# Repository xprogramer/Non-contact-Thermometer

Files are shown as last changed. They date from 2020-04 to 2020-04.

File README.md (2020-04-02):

# Non-contact-Thermometer v1.0
A low cost non-contact (infrared) Thermometer mainly based on Arduino and MLX90614 infrared temperature sensor

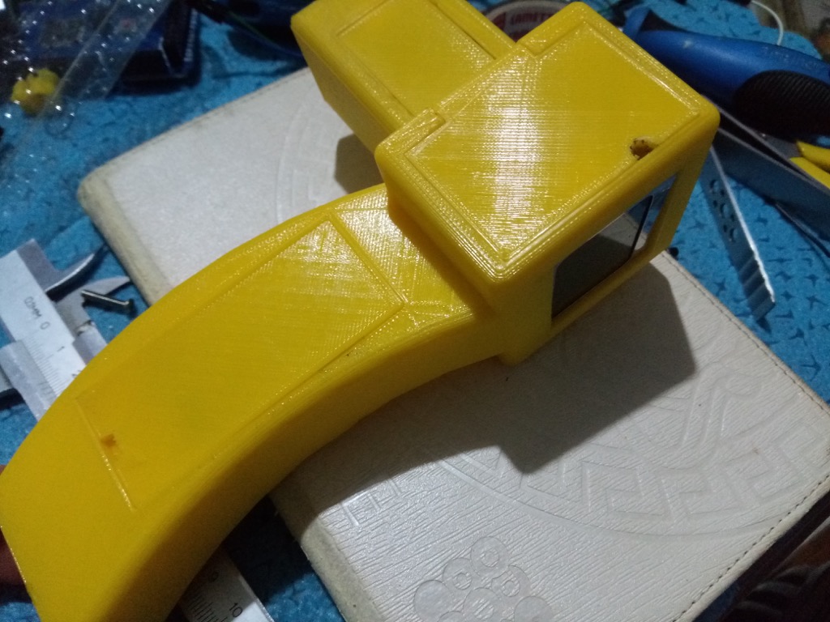
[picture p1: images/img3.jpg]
Infrared Thermometer image description


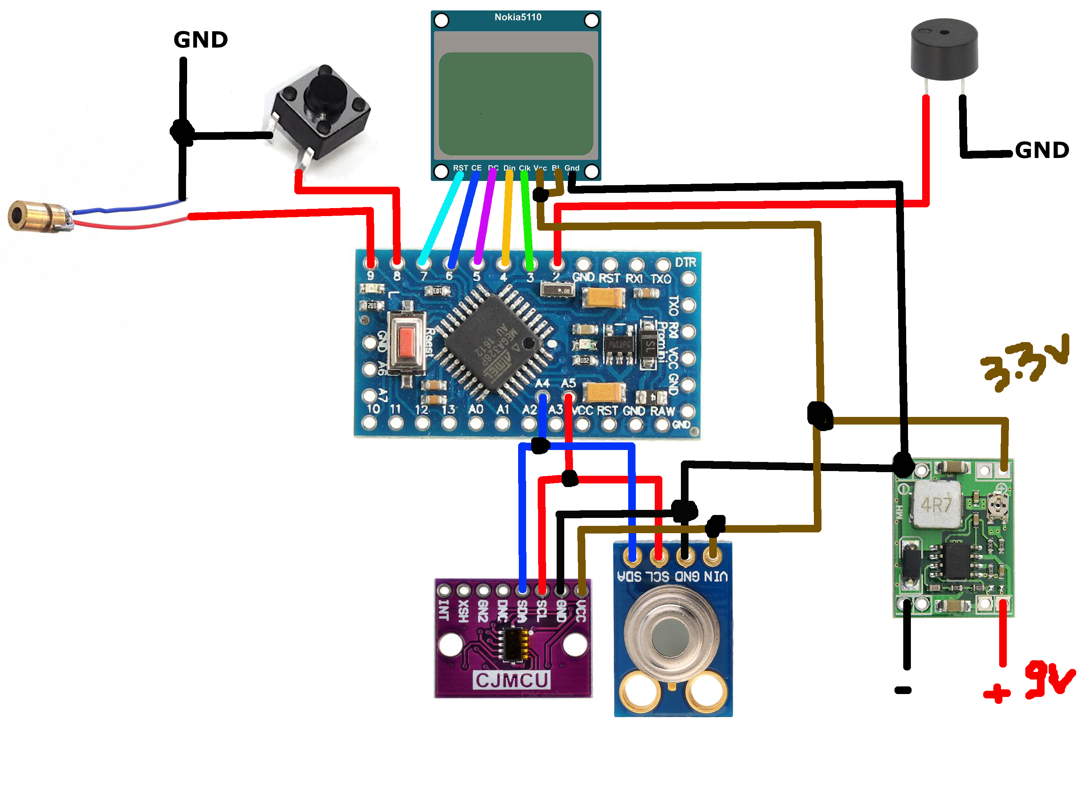
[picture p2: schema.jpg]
Wiring schema image description


# Table of contents
* [Overview](#overview)
* [Features](#features)
* [Hardware](#hardware)
* [Memory](#memory)
* [Perspectives](#perspectives)

# Overview
This project is about a non-contact thermometer that measures the object temperatures without touching them. The project is mainly based on Arduino nano, MLX90614 infrared temperature sensor and some other hardwares (check the list below). The whole hardware is embedded within a pistol, and the latter has been printed using a 3D printer. This thermometer includes a pointing laser to figure out the direction of the pistol, and does not point necessarily to the targeted point that we want to measure its temperature.
If the device is powered with sufficient current, and all the sensors are properly initialized, the buzzer makes two beeps. Conversely, the buzzer makes three beeps continuously and the screen show an error message.
In the illustrated prototype, I have used Arduino pro mini instead of Arduino nano, because I do not have Arduino nano with Mega328 micro-controller.

# Features
The Nokia 5110 LCD has been used in this project to benefit from its size and features, where we can draw anything including figures, graphs and different shapes. Another particularity of this project is the use of distance sensor (i.e. VL53L0X) to measure the distance between the pistol and the target point. The main reason to measure the distance is to avoid the contact with objects, and to the end it is very useful in the case of infected persons/objects (e.g. Covid-19). We draw the distance from the target (cm), the ambient temperature (°C) and the object temperature (°C). 

# Hardware
- The pistol model is made using a 3D printer and designed for Arduino nano. On the right side of the pistol, there is a rectangular hole to fit the USB connector of the Arduino. It was designed to make an update of the software without opening the cover, and to log data into the computer as well.
- The device uses MLX90614 sensor to measure the object temperature and the ambient temperature. It works using I2C protocol.
- The device uses VL53L0X sensor to measure the distance from the targeted object. This sensor based on time of flight technology that makes it accurate in contrast to other technologies (e.g. ultrasonic sensor). This sensor could be replaced with its upgraded sensor VL6180X to get more accurate distance (both use I2C protocol).
- The laser diode has been used to show the direction of the pistol and the target object. It points on the targeted surface (e.g. forehead) and does not point on the targeted point.
_ The voltage regulator MP1584 is used to draw a constant voltage 3.3v used to power-up the sensors and the screen.
- The push button is used to swap from IDLE to active mode and vice-versa.
- The switch button to power on/power off the device.
- A 9v battery to power the system.

# Memory
The current program (v1.0) uses approximately 22.9k of program memory, which requires a micro-controller with 30k of memory at least. In the case of Atmega328, it uses 74% of program memory and 57% of dynamic memory. It is worth mentioning that once the dynamic memory exceeds 75%, the Arduino program becomes instable. Adafruit VL53L0X library is expensively consuming, where it takes 17.3k of program memory, whereas Adafruit MLX90614 library takes 5.3k of program memory.

# Perspectives
The major limit of the current version of this device is the power consumption, where it draws important current because of the laser and the screen lights. In addition, I did not take into consideration the 3D printing errors during the CAD design, where I have found some issues to embed all the electronics (especially the screw holes). The electronic part of the push button has not been taken into consideration in the CAD design.
The minimal working distance of VL53L0X is approximately 20mm, and we must take this limit into consideration to show the real distance between the pistol and the targeted object.
As an important drawback in the current version is the buzzer tone. As we use the delay function to make a ring, we make a small blockage for a period of time, and consequently releasing the push button will not power off the laser and nor change the screen.

As perspectives for further improvements:
- Implement a minimal library for VL53L0X sensor to reduce the program size and to run on the most of micr-ocontrollers;
- Add a light sensor to manage the screen lights;
- Make ergonomic design of the pistol;
- Measure the battery level and show it on the screen;
- Implement an independent buzzer ring system to overcome the blockage;
- Design a circuit using PIR infrared (D203S) instead of MLX90614 to reduce the total cost;
- Reduce the laser power to optimise the power consumption;
- It will be better to design a PCB to reduce the wire lengths and quantity.

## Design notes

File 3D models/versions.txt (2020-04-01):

# Version 1.0
---------------
The right hole is designed for VL53L0X sensor, and it is recommended to remove the cylinders to avoid any noise. 
It is the same thing for the MLX90614 sensor. The major limit of this design is the push button, where I did not 
take into consideration the electronic part of the push button (embedding the mini push button in the 3D model). 
It is highly recommended to make a small margin of +1 -1 mm in the design (holes) to overcome the 3D printing errors.

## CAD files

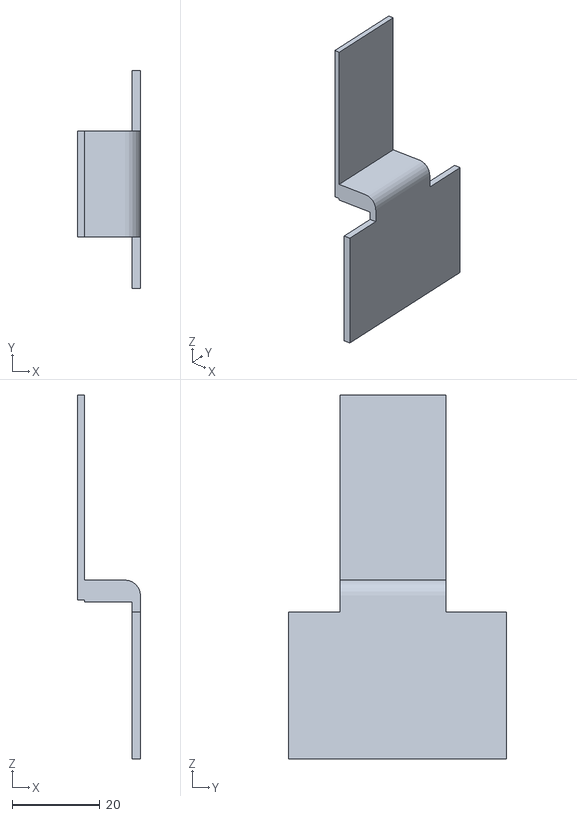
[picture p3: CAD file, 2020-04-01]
3D models/top cover.stl
14.4 x 49.5 x 82.8

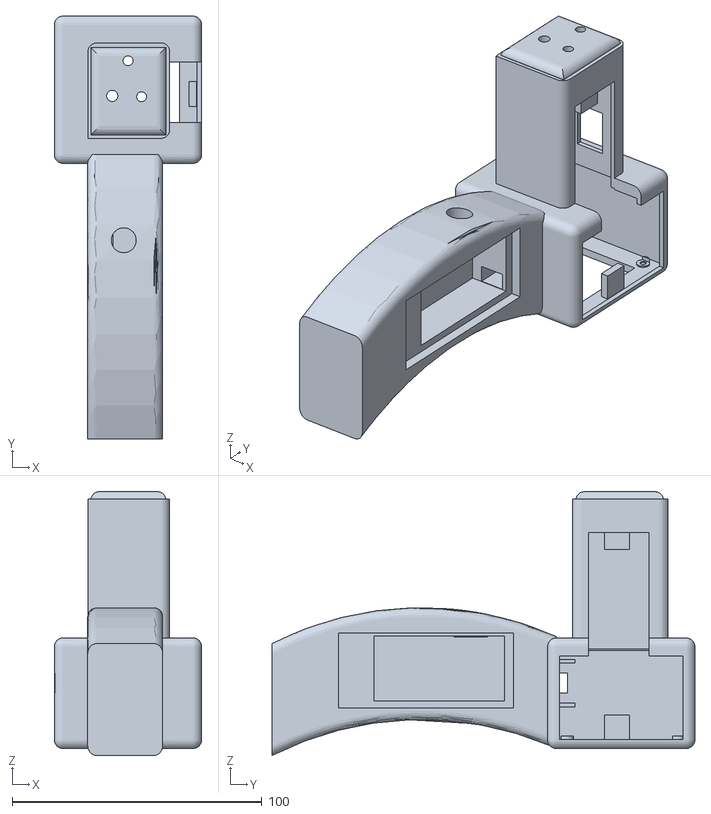
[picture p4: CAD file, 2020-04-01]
3D models/pistol.stl
59.0 x 169.2 x 105.6

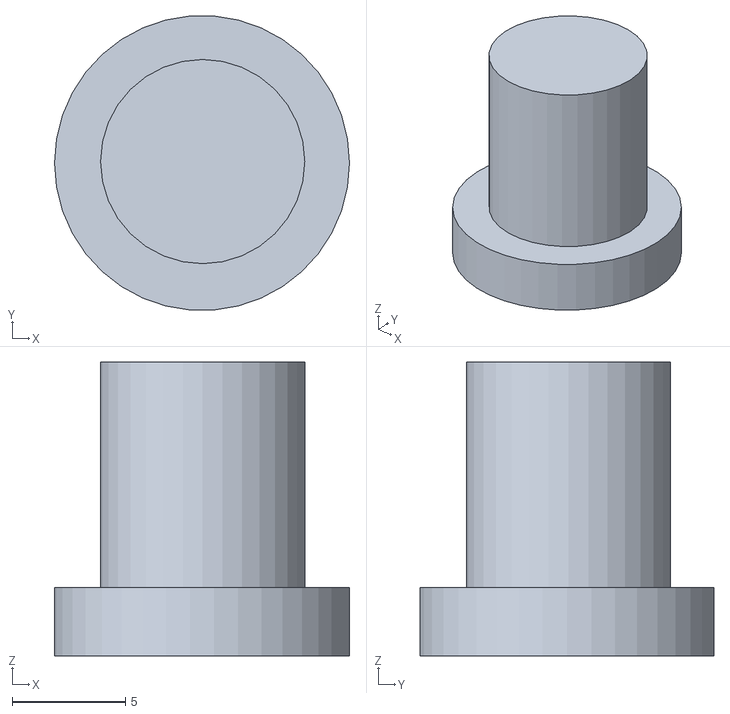
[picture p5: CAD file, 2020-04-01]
3D models/push button.stl
13.0 x 13.0 x 12.9

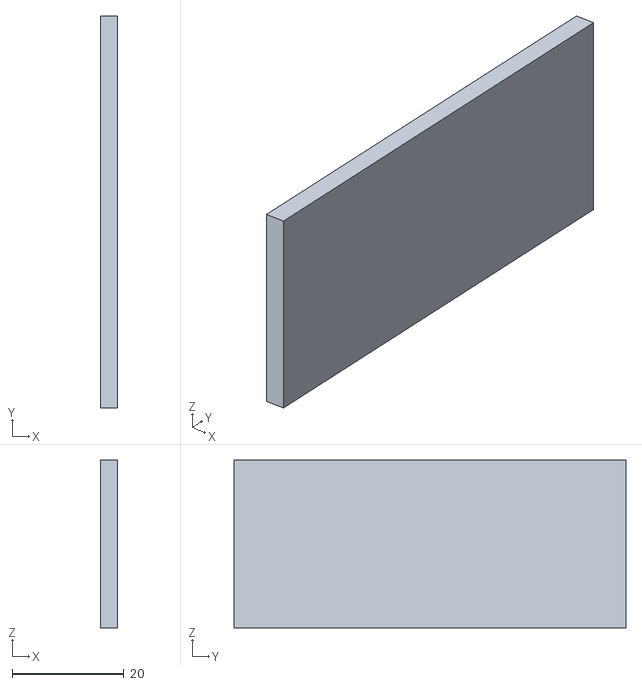
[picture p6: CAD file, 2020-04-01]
3D models/battery cover.stl
3.00 x 70.0 x 30.0

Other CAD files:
3D models/thermometer.dwg

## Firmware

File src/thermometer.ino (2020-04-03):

/**
  Author: x-programer (Abainia Kheireddine)
  Email: k.abainia@gmail.com
  Non-contact Thermometer v1.0

  This is a low cost non-contact (infrared) thermometer
  based on Arduino. The overall program uses 23k of memory,
  which requires Mega328 microcontroller at least to support
  the program. This project uses Adafruit library for the
  VL53L0X sensor, and this library is expensively consuming 
  (17k of memory). This thermometer also measures the distance
  of the targeted object, and to this end, a time of flight distance
  sensor (VL53L0X) is used and could be replaced with its improved
  version (e.g. VL6180X).
**/

#include <Wire.h>
#include <Adafruit_MLX90614.h>
#include "Adafruit_VL53L0X.h"
#include "printing_functions.h"

// comment if you don't want to use Serial Monitor
//#define __DEBUG_

#define BUZZER_PIN 2
#define BUTTON_PIN 8
#define LASER_PIN 9

#define DIST_OFFSET 1.7 // to be adjusted depending on your design
                        // because the minimal working distance of
                        // VL53L0X is 20 mm
#define TEMPERATURE_THRESHOLD 38 // the human normal temperature
                                 // does not exceed 38 °C

Adafruit_MLX90614 mlx = Adafruit_MLX90614();
Adafruit_VL53L0X lox = Adafruit_VL53L0X();

void highTemperatureAlarm();
void failAlarm();
void successAlarm();

// global variables
bool init_failed = false; // init status
bool active = false; // control button
float dist; //object distance

void setup() {
  #ifdef __DEBUG_
    Serial.begin(9600);
    Serial.println("Starting the system");
  #endif
  // configure the buzzer pin as output
  pinMode(BUZZER_PIN, OUTPUT);
  // configure the measure button as input
  pinMode(BUTTON_PIN, INPUT_PULLUP);
  // configure the laser pin as output
  pinMode(LASER_PIN, OUTPUT);
  // configure the screen
  LCD_setup();
  // initialize the MLX90614 sensor
  if (!mlx.begin()) {
    init_failed = true;
    #ifdef __DEBUG_
      Serial.println("Failed to initialize MLX90614");
    #endif
  }
  // initialize the VL53L0X sensor
  if (!lox.begin()) {
    init_failed = true;
    #ifdef __DEBUG_
      Serial.println("Failed to initialize VL53L0X");
    #endif
  }
  if(init_failed) {
    #ifdef __DEBUG_
      Serial.println("Initialization is failed !");
    #endif
    // alarm an error
    failAlarm();
  }
  else {
    #ifdef __DEBUG_
      Serial.println("[ Successfully initialized ]");
    #endif
    // alarm a success
    successAlarm();
  }
  clear();
}

void loop() {
  if(digitalRead(BUTTON_PIN) == LOW) {
      active = true;
      digitalWrite(LASER_PIN, HIGH);
      clear();
  }
  else {
      active = false;
      digitalWrite(LASER_PIN, LOW);
      clear();
  }
  // if the initialization failed    
  if(init_failed) {
    setCursor(25,2);
    printChar(0x7f, 0x49, 0x49, 0x49, 0x41); // print E
    printChar(0x7c, 0x08, 0x04, 0x04, 0x08); // print r
    printChar(0x7c, 0x08, 0x04, 0x04, 0x08); // print r
    printChar(0x38, 0x44, 0x44, 0x44, 0x38); // print o
    printChar(0x7c, 0x08, 0x04, 0x04, 0x08); // print r
    printChar(0x00, 0x00, 0x00, 0x00, 0x00); // print sapce
    printChar(0x00, 0x00, 0x5f, 0x00, 0x00); // print !
    failAlarm();
  }
  // if the initialization is done and the measure button is pressed
  else if(active) {
    setCursor(1,5);
    VL53L0X_RangingMeasurementData_t measure;
    printDistance(); // print "Distance"
    setCursor(54,5);
    lox.rangingTest(&measure, false);
    
    if (measure.RangeStatus != 4) {  
      dist = (float)measure.RangeMilliMeter / 10;
      dist -= DIST_OFFSET;
      #ifdef __DEBUG_
        Serial.print("Distance (cm): ");
        Serial.println(dist);
      #endif
    }
    else {
      #ifdef __DEBUG_
        Serial.println(" out of range ");
      #endif
      dist = 99999;
    }
    // print the distance value
    printFloatNumber(dist);
  
    setCursor(2,0);
    printAmbient(); // print "Ambient"
    setCursor(40,0);
    // read the ambient temperature
    float deg;
    deg = mlx.readAmbientTempC();
    // print the ambient temperature
    printFloatNumber(deg, true);
    #ifdef __DEBUG_
      Serial.print("Ambient temperature (°C) :  ");
      Serial.println(deg);
    #endif
    // read the object temperature
    deg = mlx.readObjectTempC();
    // print the object temperature
    printObjectDeg(deg);
    #ifdef __DEBUG_
      Serial.print("Object temperature (°C) :  ");
      Serial.println(deg);
    #endif
    if(deg > TEMPERATURE_THRESHOLD) {
      highTemperatureAlarm();
    }
    delay(1000);
  }
  // if the measure button is not pressed
  else {
    #ifdef __DEBUG_
      Serial.println("Ready to measure..Press the button !");
    #endif
    setCursor(25,2);
    printChar(0x7f, 0x09, 0x19, 0x29, 0x46); // print R
    printChar(0x7f, 0x49, 0x49, 0x49, 0x41); // print e
    printChar(0x20, 0x54, 0x54, 0x54, 0x78); // print a
    printChar(0x38, 0x44, 0x44, 0x48, 0x7f); // print d
    printChar(0x0c, 0x50, 0x50, 0x50, 0x3c); // print y
    printChar(0x00, 0x00, 0x00, 0x00, 0x00); // print space
    printChar(0x00, 0x00, 0x5f, 0x00, 0x00); // print !
    delay(500);
  }
}


void highTemperatureAlarm() {
  tone(BUZZER_PIN,1000);
  delay(2000);
  noTone(BUZZER_PIN);
}

void successAlarm() {
  tone(BUZZER_PIN,1000);
  delay(500);
  tone(BUZZER_PIN,500);
  delay(500);
  noTone(BUZZER_PIN);
  delay(1000);
}

void failAlarm() {
  tone(BUZZER_PIN,1000);
  delay(300);
  noTone(BUZZER_PIN);
  delay(500);
  tone(BUZZER_PIN,700);
  delay(300);
  noTone(BUZZER_PIN);
  delay(500);
  tone(BUZZER_PIN,1000);
  delay(300);
  noTone(BUZZER_PIN);
  delay(1000);
}

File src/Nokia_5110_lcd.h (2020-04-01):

#ifndef NOKIA_5110_LCD_H
#define NOKIA_5110_LCD_H

#define LCD_CLK 3
#define LCD_SDA 4
#define LCD_DC 5
#define LCD_SCE 6
#define LCD_RST 7

void sendCmd(byte _val) {
   digitalWrite(LCD_DC,0);
   digitalWrite(LCD_SCE, LOW);
   for(int i=7; i>=0; i--) {
      digitalWrite(LCD_CLK, LOW);
	    digitalWrite(LCD_SDA, bitRead(_val, i));
      digitalWrite(LCD_CLK, HIGH);
   }
   digitalWrite(LCD_SCE, HIGH);
}

void sendData(byte _val) {
   digitalWrite(LCD_DC,1);
   digitalWrite(LCD_SCE, LOW);
   for(int i=7; i>=0; i--) {
      digitalWrite(LCD_CLK, LOW);
      digitalWrite(LCD_SDA, bitRead(_val, i));
      digitalWrite(LCD_CLK, HIGH);
   }
   digitalWrite(LCD_SCE, HIGH);
}

void setCursor(byte column, byte line) {
    sendCmd(0x80 | column);
    sendCmd(0x40 | line);
}

void clear() {
  setCursor(0, 0);
  for (unsigned short i = 0; i < 580; i++)
    sendData(0x00);
  setCursor(0, 0);
}

void LCD_setup() {
	pinMode(LCD_CLK,OUTPUT);
	pinMode(LCD_SDA,OUTPUT);
	pinMode(LCD_DC,OUTPUT);
	pinMode(LCD_RST,OUTPUT);
	pinMode(LCD_SCE,OUTPUT);
	
	digitalWrite(LCD_RST,HIGH);
	digitalWrite(LCD_SCE,HIGH);
	digitalWrite(LCD_RST,LOW);
	delay(100);
	digitalWrite(LCD_RST,HIGH);
	
	// Set the LCD parameters...
	sendCmd(0x21); // extended instruction set control (H=1)
	sendCmd(0x13); // bias system (1:48)
	sendCmd(0xc2);  // default Vop (3.06 + 66 * 0.06 = 7V)
	sendCmd(0x20); // extended instruction set control (H=0)
	sendCmd(0x09); // all display segments on
	// Clear the screen
  clear();
	// Activate LCD...
	//sendCmd(0x08); // display blank
	sendCmd(0x0c); // normal mode (0x0d = inverse mode)
  delay(100);
  sendCmd(0x80);
  sendCmd(0x40);
}

void printChar(byte b1,byte b2,byte b3,byte b4,byte b5) {
	sendData(b1);
	sendData(b2);
	sendData(b3);
	sendData(b4);
	sendData(b5);
	sendData(0x00);
}

void printChar2(byte b1,byte b2,byte b3,byte b4,byte b5,byte b6,byte b7,byte b8,byte b9,byte b10) {
  sendData(b1);
  sendData(b2);
  sendData(b3);
  sendData(b4);
  sendData(b5);
  sendData(b6);
  sendData(b7);
  sendData(b8);
  sendData(b9);
  sendData(b10);
  sendData(0x00);
  sendData(0x00);
}

void printSimpleNumber(byte num) {
  switch(num) {
    case 0:
      printChar(0x3e, 0x51, 0x49, 0x45, 0x3e);
      break;
    case 1:
      printChar(0x00, 0x42, 0x7f, 0x40, 0x00);
      break;
    case 2:
      printChar(0x42, 0x61, 0x51, 0x49, 0x46);
      break;
    case 3:
      printChar(0x21, 0x41, 0x45, 0x4b, 0x31);
      break;
    case 4:
      printChar(0x18, 0x14, 0x12, 0x7f, 0x10);
      break;
    case 5:
      printChar(0x27, 0x45, 0x45, 0x45, 0x39);
      break;
    case 6:
      printChar(0x3c, 0x4a, 0x49, 0x49, 0x30);
      break;
    case 7:
      printChar(0x01, 0x71, 0x09, 0x05, 0x03);
      break;
    case 8:
      printChar(0x36, 0x49, 0x49, 0x49, 0x36);
      break;
    case 9:
      printChar(0x06, 0x49, 0x49, 0x29, 0x1e);
      break;
  }
}

void printGrandNumber(byte num, byte column=0, byte line=0) {
  if(num == 0)
  {
    setCursor(column, line);
    printChar2(0xfc, 0xfc, 0x03, 0x03, 0x03, 0x03, 0x03, 0x03, 0xfc, 0xfc);
    setCursor(column, line+1);
    printChar2(0x3f, 0x3f, 0xc0, 0xc0, 0xc0, 0xc0, 0xc0, 0xc0, 0x3f, 0x3f);
  }
  if(num == 1)
  {
    setCursor(column, line);
    printChar2(0x00, 0x00, 0x0C, 0x0C, 0xff, 0xff, 0x00, 0x00, 0x00, 0x00);
    setCursor(column, line+1);
    printChar2(0x00, 0x00, 0xC0, 0xC0, 0xff, 0xff, 0xC0, 0xC0, 0x00, 0x00);
  }
  if(num == 2)
  {
    setCursor(column, line);
    printChar2(0x0c, 0x0e, 0x07, 0x03, 0x03, 0x03, 0x83, 0xc7, 0x7e, 0x3c);
    setCursor(column, line+1);
    printChar2(0xf0, 0xfc, 0xde, 0xc6, 0xc7, 0xc3, 0xc3, 0xc1, 0xc0, 0xc0);
  }
  if(num == 3)
  {
    setCursor(column, line);
    printChar2(0x00, 0x00, 0x83, 0x83, 0x83, 0x83, 0x83, 0x83, 0x7c, 0x7c);
    setCursor(column, line+1);
    printChar2(0x00, 0x00, 0xc1, 0xc1, 0xc1, 0xc1, 0xc1, 0xc1, 0x3e, 0x3e);
  }
  if(num == 4)
  {
    setCursor(column, line);
    printChar2(0x00, 0xc0, 0xf0, 0x3d, 0xf, 0x03, 0xff, 0xff, 0x00, 0x00);
    setCursor(column, line+1);
    printChar2(0x0f, 0x0f, 0x0c, 0x0c, 0x0c, 0x0c, 0xff, 0xff, 0x0c, 0x0c);
  }
  if(num == 5)
  {
    setCursor(column, line);
    printChar2(0xff, 0xff, 0x03, 0x03, 0x03, 0x03, 0x03, 0x03, 0x03, 0x03);
    setCursor(column, line+1);
    printChar2(0xc3, 0xc3, 0xc3, 0xc3, 0xc3, 0xc3, 0x63, 0x63, 0x3e, 0x3e);
  }
  if(num == 6)
  {
    setCursor(column, line);
    printChar2(0xc0, 0xf0, 0x38, 0x1c, 0x0e, 0x06, 0x03, 0x03, 0x03, 0x00);
    setCursor(column, line+1);
    printChar2(0x7f, 0xff, 0xe7, 0xc3, 0xc3, 0xc3, 0xc3, 0xe7, 0x7e, 0x3c);
  }
  if(num == 7)
  {
    setCursor(column, line);
    printChar2(0x03, 0x03, 0x03, 0x03, 0xC3, 0xC3, 0x33, 0x33, 0x0f, 0x0f);
    setCursor(column, line+1);
    printChar2(0x00, 0x00, 0xff, 0xff, 0x00, 0x00, 0x00, 0x00, 0x00, 0x00);
  }
  if(num == 8)
  {
    setCursor(column, line);
    printChar2(0x7c, 0x7c, 0x83, 0x83, 0x83, 0x83, 0x83, 0x83, 0x7c, 0x7c);
    setCursor(column, line+1);
    printChar2(0x3e, 0x3e, 0xc1, 0xc1, 0xc1, 0xc1, 0xc1, 0xc1, 0x3e, 0x3e);
  }
  if(num == 9)
  {
    setCursor(column, line);
    printChar2(0x3c, 0x7e, 0xe7, 0xc3, 0xc3, 0xc3, 0xc3, 0xe7, 0xfe, 0xfc);
    setCursor(column, line+1);
    printChar2(0x00, 0xc0, 0xc0, 0xc0, 0x60, 0x70, 0x38, 0x1c, 0x0f, 0x03);
  }
}

#endif

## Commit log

2020-04-01 Add the STL file of the battery cover
    [battery cover.stl]
2020-04-01 Add the STL file of the push button
    [push button.stl]
2020-04-01 Add the STL file of the pistol
    [pistol.stl]
2020-04-01 Add the STL file of the top cover
    [top cover.stl]
2020-04-01 Add the Autocad 3D model
    [thermometer.dwg]
2020-04-01 Update versions.txt
    Briefly discuss the limits of the current 3D design
2020-04-01 Add assembly photos
    Photos taken during the assembly phase
2020-04-01 Add error video
    A video showing an error detected by the system and is due to low battery
2020-04-01 Add video of good starting
    A video showing a good starting of the device with two Bips and "ready" message on the screen
2020-04-02 Add wiring schema
2020-04-02 Update the readme
    Include the image of the wiring schema
2020-04-02 Add more descriptions
    Discuss the current features, limits and some perspectives
